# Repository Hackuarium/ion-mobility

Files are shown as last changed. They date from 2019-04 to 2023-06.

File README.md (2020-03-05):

# What is Ion Mobility Spectrometry ?

[https://en.wikipedia.org/wiki/Ion-mobility_spectrometry]

# Why should we do this ?

There are numerous application for IMS and it has the main advantage to work at atmospheric pressure (in constraste with mass spectrometry that requires most of the time 10-3 torr) that would make it compact and affordable.

We see the possibility to make continious monitoring of the bioreactor made by Hackuarium and situated in Cali, Colombia.

# Can we do a Ion Mobility Spectrometer our self ?

Main parts of the IMS :

- Desolvation zone : Insert and ionization of sample. 
Electrospray ionisation (ESI). Advantage : one can insert the liquid sample and ionize it through the same needle. 
Limitation : 5kV voltage source, 100uL/min flow rate through the needle. 

- Shutter : Let the ions pass on command.
Three grid Shutter. Advantage : easy to built and to command. 

- Drift zone : Acceleration of ions.
Made by multiple electrodes connected to different voltages with the aid of a voltage divider. 
Limitation : 10kV voltage source. 

- Detection : Faraday plate.
Transconductance amplifier converts the tiny ion current into a reasonable tension.
Limitation : The current-to-tension AOP must be with very low bias current, and low noise (hence expensive). 

- Monitoring : A/D converter. 

Link to full project already made : [https://github.com/bhclowers/OS-IMS]

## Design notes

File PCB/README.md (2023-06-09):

In order to better understand the overall electrical diagram and the paper’s resistance choice, an equivalent electrical diagram of the IMS from the first electrode to the amplifier is shown below. 
<p align="center">
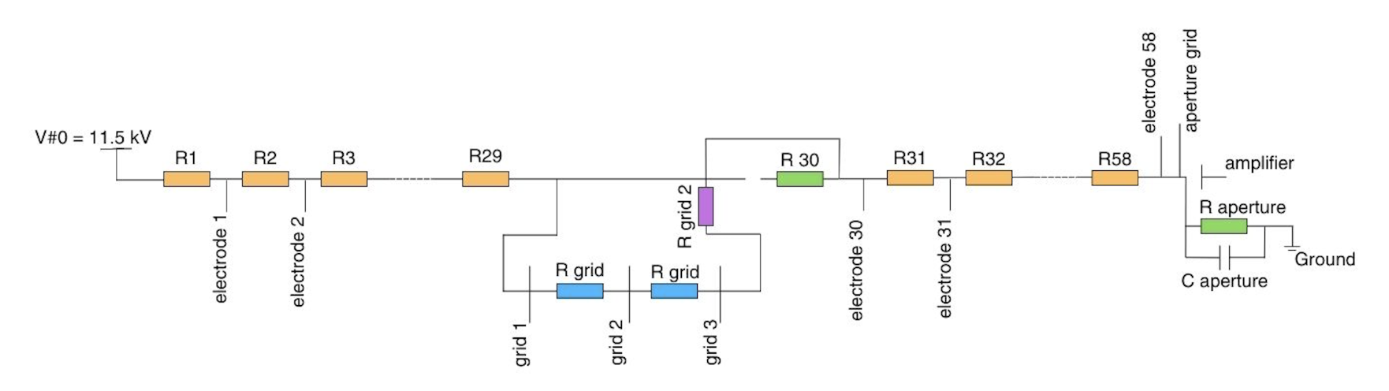
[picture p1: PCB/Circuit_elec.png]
    
</p>

Thanks to those equations, we see that when the gate is closed, the potential of the second grid is higher than when it is opened. In the paper, they recommend adding 30 to 80 V (referenced to ”small” in the equations) to stop the flow of electrons. According to the calculations, a value of 50V or higher would result in a reverse electric field and effectively close the gate. 

These calculations are based on the paper’s values, not those of the current prototype. For the moment, the resistors on the divider PCB are 10 MΩ, designed to reduce power consumption. But this does not seem necessary, since with 1 MΩ resistors, power consumption is already only 160 to 200 μA, and changing the resistor of the dividers would also mean adapting the other resistors of the circuit.

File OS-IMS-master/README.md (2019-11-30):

# APIMS
Atmospheric Pressure Ion Mobility Design

The design files located in this repository comprise the working design files used for the atmospheric pressure ion mobility spectrometer operated at Washington State University (Dr. Brian Clowers) and Azuza Pacific University (Dr. Eric Davis). Periodic updates will be pushed as modifications are made.  A wiki will be populated for the next version of the system is constructed to provide other researchers with a detailed set of assembly instructions. 

<p align="center">

</p>

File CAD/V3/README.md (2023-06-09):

# CAD design files

## Description

This folder contains all CAD design files for the V3 3D printed version of the IMS. This version is designed to hold the electrodes together in place with the divider PCBs, the target and an extension to choose the number of electrodes wanted (29 per region). It's an upgraded version of V2, capable of accommodating the 3-grid ion shutter, the aperture grid and a chamber on the backside of the target for the inlet drift/carrier gas.

It is designed to be modulary and partially modified if necessary without needing to redo and reprint the whole device.

- All the files are in 3 different versions : 
1. .SLDPRT, aka Solidworks (software used initially)
2. .STEP, to be able to open them in most CAD softwares
3. .3mf, the standard manufacturing file to 3D print with a FDM printer (e.g. prusa)

NB: The "Cible" (i.e. target) and electrode PCBs are the same one as in the V2 version, thus they are the same files as in the V2 folder. The divider PCB is different, because it is the 29 electrode slots version, as per the paper.

## Specifications

The desolvation and drift regions can hold 29 electrodes each.  
Every 2 electrodes have the same distance in between them, i.e. 0.8 mm. This ensures that the electric field is linear and continuous throughout the whole device.

The ESI needle (needs to be 3-4 kV higher in potential than the first electrode) can be mounted in front of the desolvation region.

A Nafion membrane is commonly used in IMS to separate ionized gases from other gaseous species and prevent measurement disturbances. Here are a few reasons why this membrane is used:
1. Ion selection: the Nafion membrane is selective for H+, Na+, K+ and NH4+ cation ions. It therefore selects the ions of interest for measurement, while rejecting other non-ionized or uncharged gaseous species.
2. Gas separation: the Nafion membrane is permeable to gases, but only allows high-mobility gases such as H2, N2, O2 and H2O to pass through. It therefore prevents low-mobility gases, such as noble gases, from entering the measurement zone and interfering with the results.
3. Impurity removal: the Nafion membrane can remove impurities from gases by exchanging the cations present on its surface with the impurities. It is therefore useful for eliminating contaminants that could interfere with measurement.

In our case, the membrane is mainly used for ion selection. In fact, it allows us to have only the species of interest in our spectrometer, and therefore more reliable results. The membrane is placed between the needle and the first electrode. 

Our membrane specifications:  
*Model: Nafion 117*  
*Thickness: 183 µm*  
*Density: 360 g/m2*  
*Conductivity: 0.083 S/cm*  
*Exchange capacity: 0.89 meq/g*  
*Size: 40 mm diameter circle*  

Below is a close up picture of the exploded 3-grid ion shutter :

<p align="center">
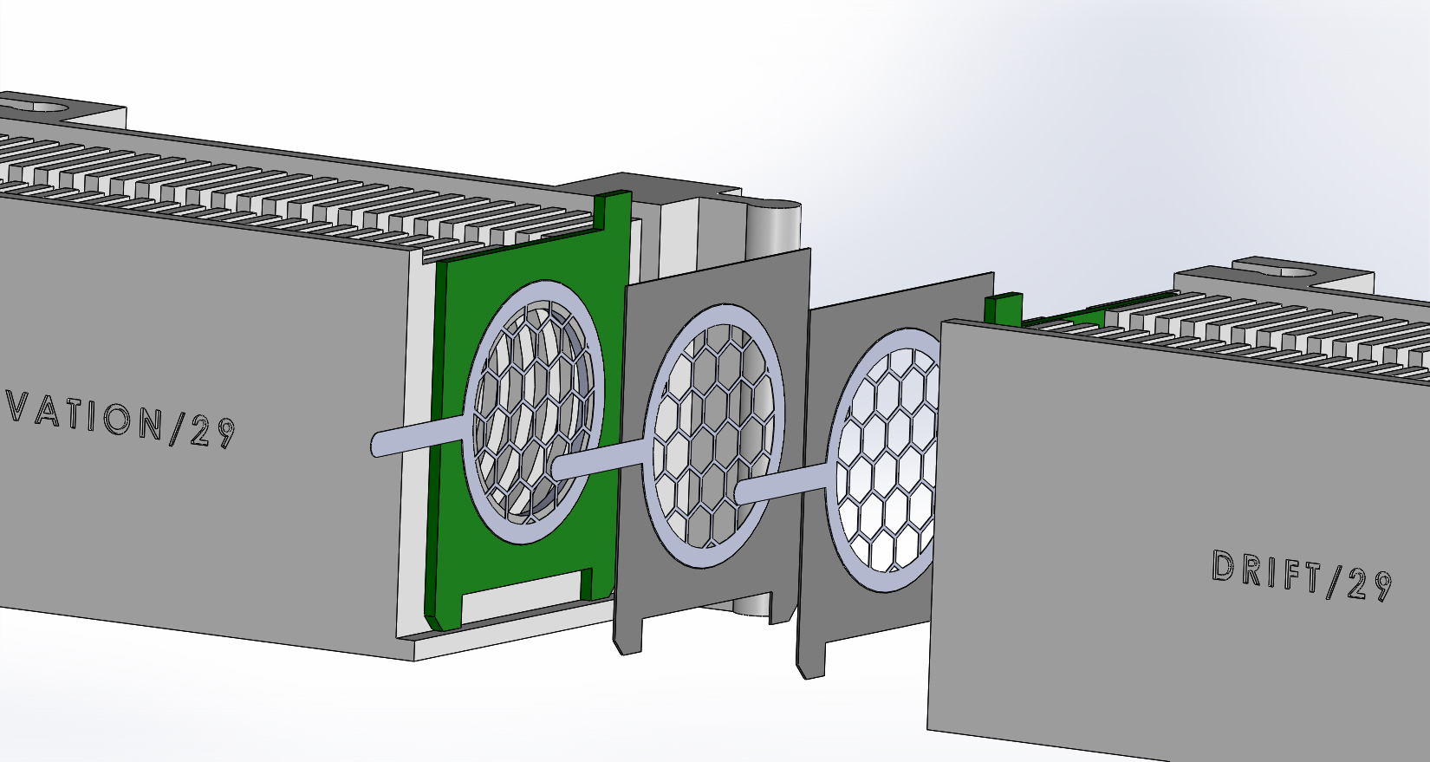
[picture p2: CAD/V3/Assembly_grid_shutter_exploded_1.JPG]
  
</p>

## Current limitations

This version hasn't been printed because we do not have the grids nor the grid spacers yet. The spacers are supposed to be 0.3mm thick, made of basically any non conductive material, and the grids are 0.1mm thick, made of stainless steel (NB: the grids in the assembly have a coarser grid with a bigger honeycomb pattern to lighten the computationnal render).

<p align="center">
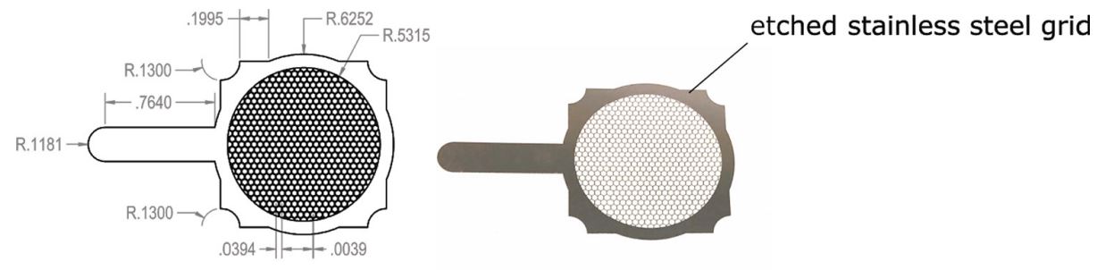
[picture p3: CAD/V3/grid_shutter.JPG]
  
</p>

## Target/Cible

The target ("Cible") is mounted at the end of the IMS, and has a hole on its back side to connect the amplification PCB as well as a hole on its top to put a tube inlet for the drift/carrier gas.

## CAD designed device

Here is shown the model of the V3 version of the CAD casing. It is a revised version with room to accommodate for the 3-grid on shutter, the aperture grid and the gas chamber for the target. The desolvation and drift regions have here 29 electrode slots each (the extension is thus not needed here and the ESI needle can be put in front directly).

<p align="center">
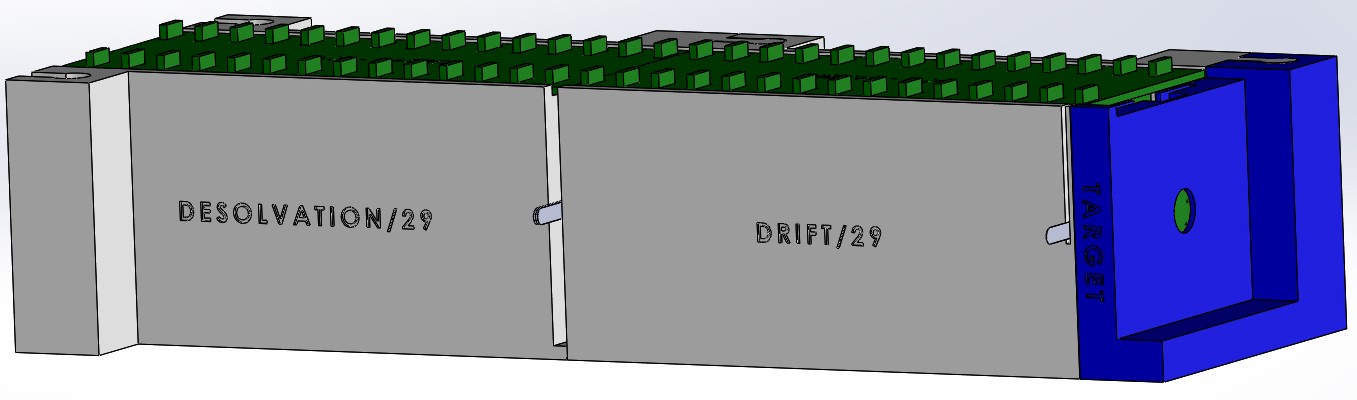
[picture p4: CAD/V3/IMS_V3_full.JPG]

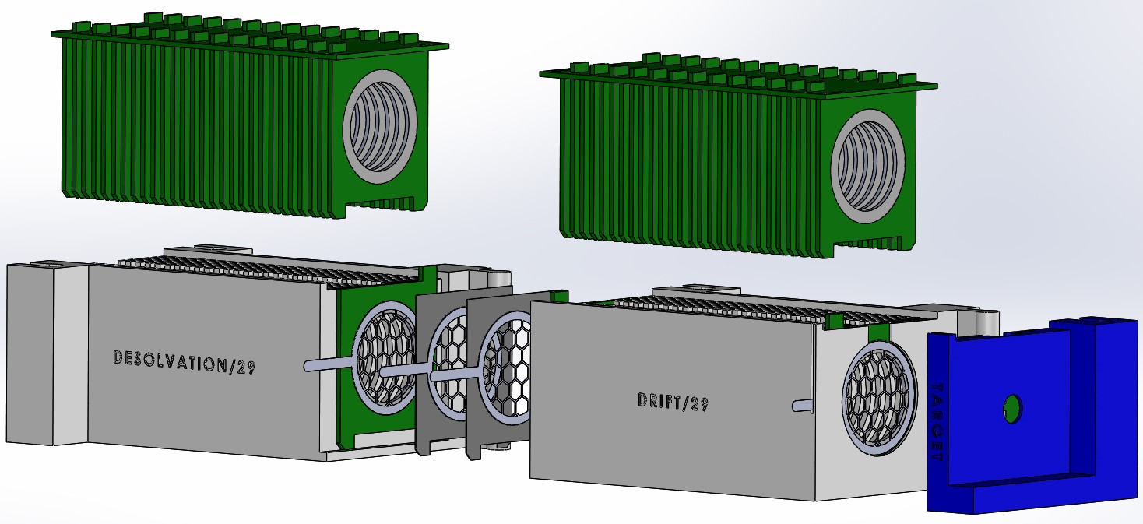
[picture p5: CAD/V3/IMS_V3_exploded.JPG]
   
</p>

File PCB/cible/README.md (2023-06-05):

# Target/Cible

## Description

Target at the end of the IMS/Drift tube, on which the ions will collide and create a small current. Is situated after the drift tube and before the amplification.

The target is a [Faraday plate](https://en.wikipedia.org/wiki/Faraday_cup) used to catch the ions and analyze them afterwards.

## Specifications and limitations

The target has to be surrounded by a ground connected ring with small holes to inject a drift gas. It is connected on its back side to the amplifier to transform the ion current into a readable voltage.

## PCB

Below are pictures of the target PCB. 

<p align="center">
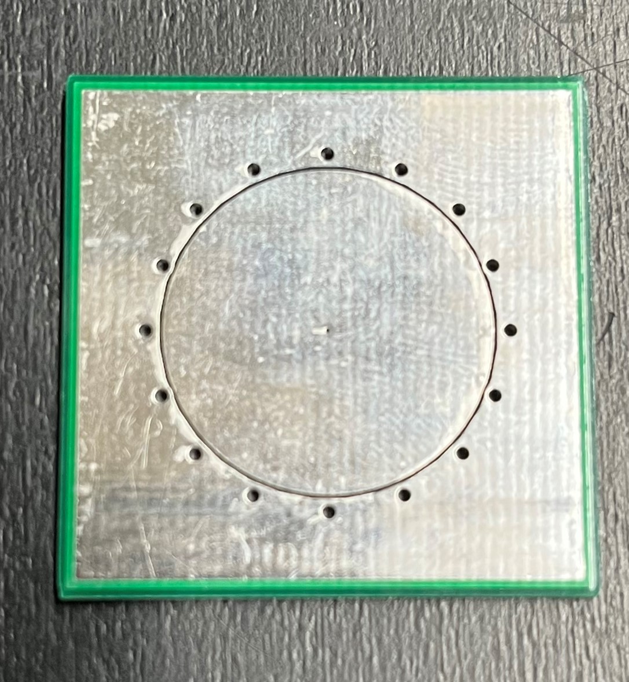
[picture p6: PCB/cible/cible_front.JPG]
    
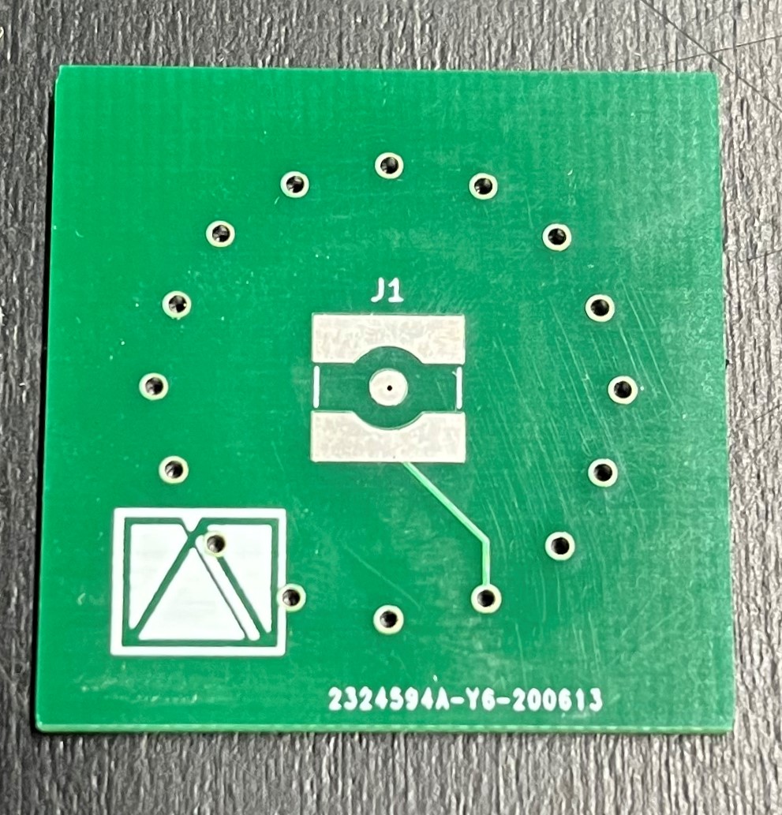
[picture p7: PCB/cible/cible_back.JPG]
    
</p>

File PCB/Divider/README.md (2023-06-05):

# Divider

## Description

Printed circuit board of the two voltage dividers for the desolvation region and the drift tube/region. Connects all electrodes together with 10 M $\Omega$ in between each of them, to create a continuous voltage gradient and thus an electric field to accelerate the ions. 

## Specifications and limitations

The highest voltage is 11.5 kV at the first electrode, down to the ground connected last electrode, and the target at the end of the drift tube.

Higher resistors in between the electrodes doesn't change the voltage gradient but reduces the current and thus the electrical consumption.

## PCB

Below are pictures of the PCBs. First one is desolvation region and second one is drift region.

<p align="center">
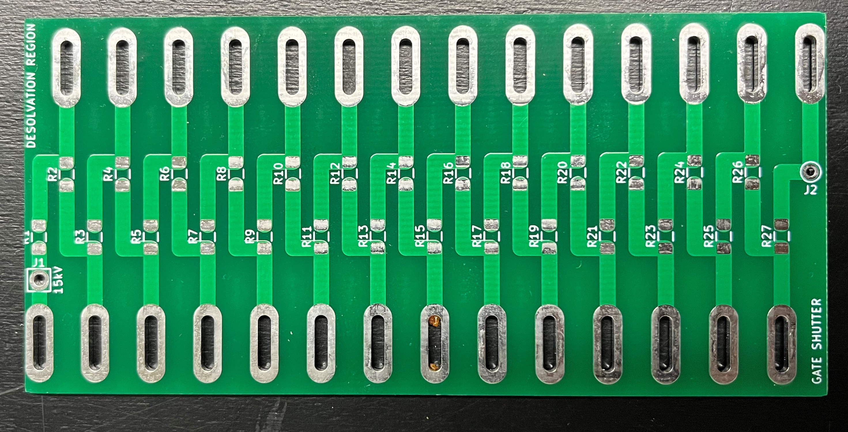
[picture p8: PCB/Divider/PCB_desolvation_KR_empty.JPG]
    
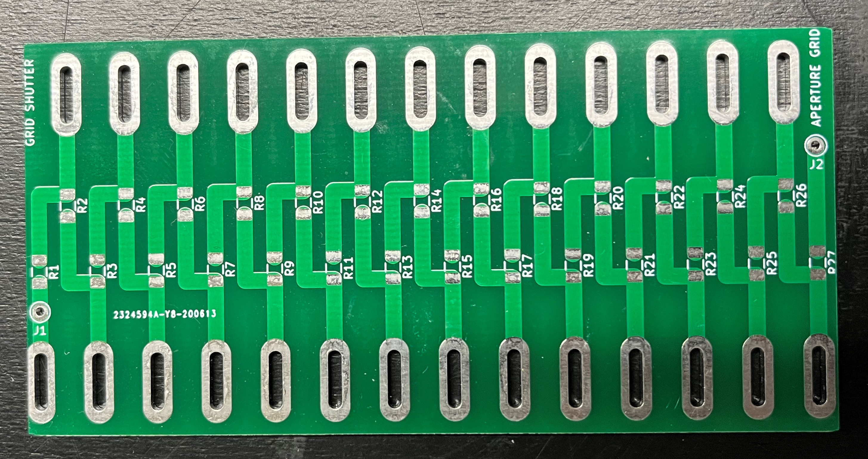
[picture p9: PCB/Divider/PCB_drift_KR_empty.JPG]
    
</p>

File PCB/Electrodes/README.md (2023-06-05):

# Electrode PCB

## Description

Here are all the PCB files related to the electrodes.

## PCB

Below is a picture of the PCB. 

<p align="center">
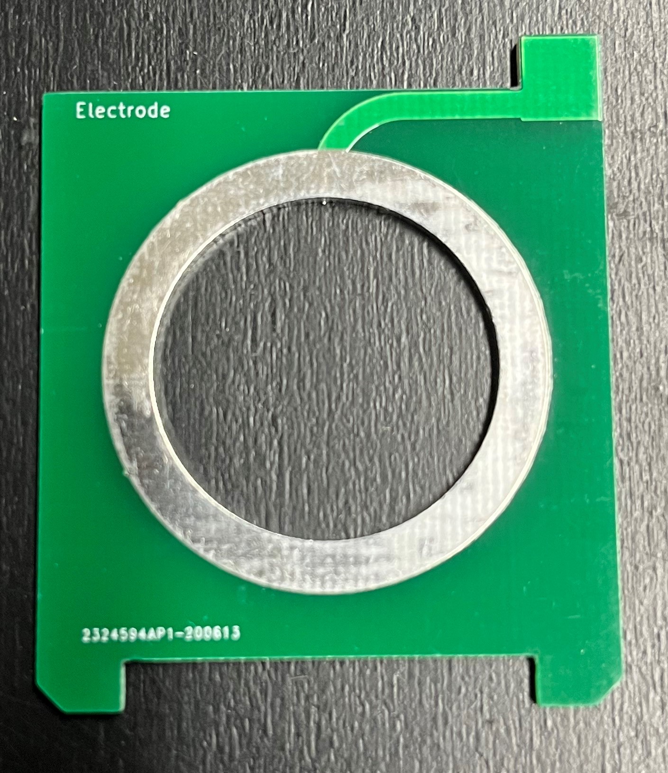
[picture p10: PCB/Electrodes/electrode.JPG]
    
</p>

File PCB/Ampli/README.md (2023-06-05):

# Amplification stage

## Description

Amplification stage to transform the small current on the target to an acceptable voltage to be read/processed. 

[Transimpedance circuit](https://en.wikipedia.org/wiki/Transimpedance_amplifier) with a big gain (10^8) and a voltage follower through a dual precision operationnal amplifier (Texas Instruments LMC6082).

## Specifications and limitations

The circuit needs to be as close as possible to the target of the IMS in order to limit the noise present on the signal. One possibility is to solder the PCB directly on the back of the target. 

Possible amplification of the noise must be taken into account, and possibly filtered through a very small capacitor (~0.01 pF, thus quite expensive) in the gain stage feedback loop (a bigger resistor amplifies the signal but also the noise).

## PCB

Below is a picture of the mounted PCB, currently missing the connectors and a potential filtering capacitor C1. 

<p align="center">
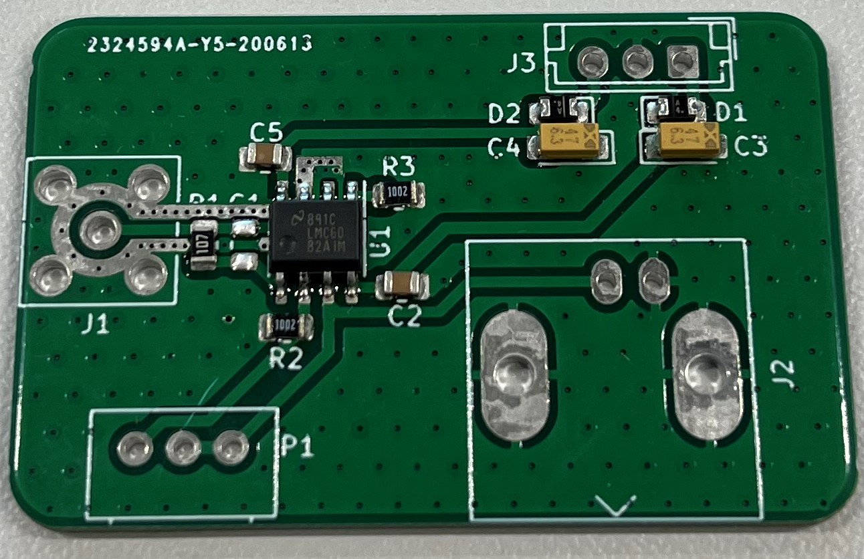
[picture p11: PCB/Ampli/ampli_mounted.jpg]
    
</p>

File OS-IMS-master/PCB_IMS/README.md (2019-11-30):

## This directory contains the latest version of the PCB IMS to be detailed in the manuscript submitted to HardwareX.  These files outline the design and assembly of a high performance, open-source Ion Mobility System

<p align="center">
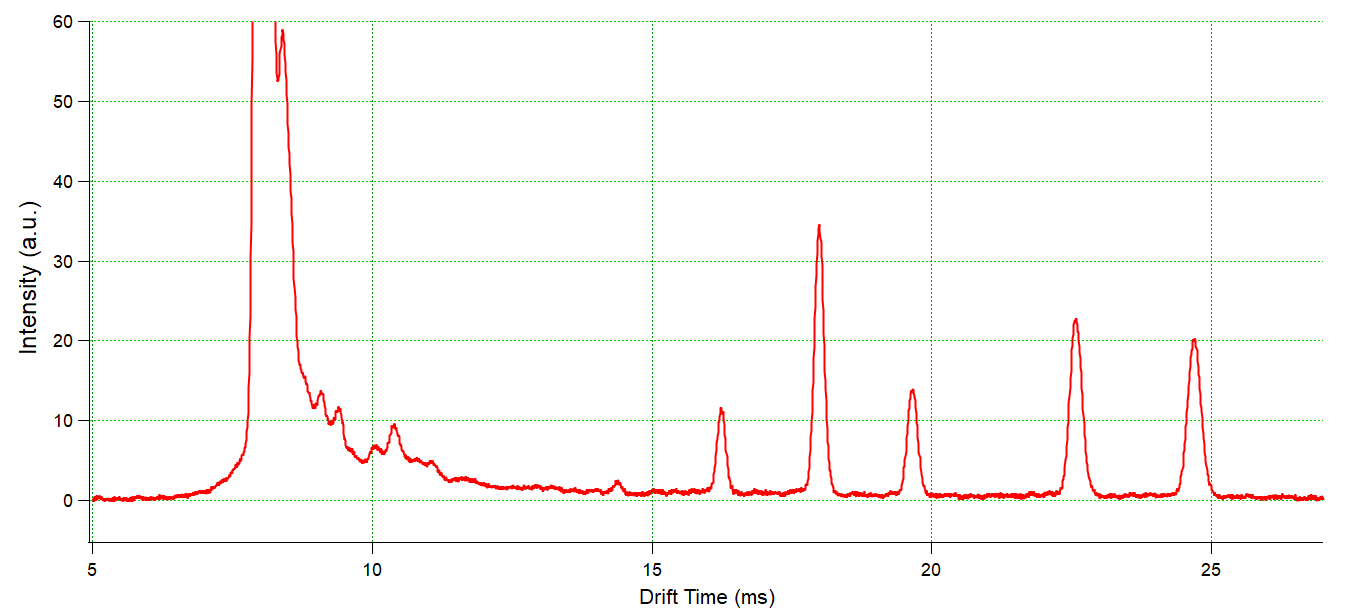
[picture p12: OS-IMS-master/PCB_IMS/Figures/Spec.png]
  </p>
</center>
<p align="center">
  </p>
</center>

#### When operated as a stand-alone device, an ion mobility spectrometer (IMS) routinely offers low limits of detection (pptv-range) for gas-phase analytes even for measurement times less than a second. Mass analyzers further enhance the analytical power of IMS separations, however, high performance drift-cell IMS instruments are often highly customized, relatively large, and require extensive expertise to operate. In this work we present an optimized, low cost IMS system that leverages an easy-to-assemble ion gating structure that enables IMS spectra with resolving powers exceeding 90 for a drift cell only 10 cm in length. The IMS presented in this work consists of stacked rings divided by spacers all fabricated from printed circuit boards (PCB). The rings are connected via a slotted PCB-board containing a surface mounted voltage divider that connects directly to the ring electrodes allowing a fast and easy assembly. This highly modular design enables e.g. the realization of variable drift tube lengths or single and dual gate setups. Instead of the commonly used Bradbury Nielsen gates, the IMS is equipped with a 3-grid ion gate allowing the generation of short (<50 μs) ion packets increasing the resolving power of the instrument. 

### License

Open Source Hardware 

The PCB-IMS is an open source project by [*Tobias Reinecke*](mailto:treinecke@gmail.com) and [*Brian Clowers*](mailto:bhclowers@gmail.com).

The use, modification, and implementation of this project is goverened by the [CERN Open Hardware Licence v1.2](LICENSE).

#### Acknowledgements:
* This work was supported in part by the National Science Foundation (CHE-1506672) and DTRA (Award Number: HDTRA1-14-1-0023)
* We would also like to acknowledge the dedicated, prolific, and timeless efforts of [*Gordon A. Anderson*](https://github.com/GordonAnderson).

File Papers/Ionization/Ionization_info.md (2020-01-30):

# Non - Radioactive ionization 

- Désorption-ionisation laser assistée par matrice : [https://fr.wikipedia.org/wiki/D%C3%A9sorption-ionisation_laser_assist%C3%A9e_par_matrice] (No gate needed?!)
- UV LED Ionization : [UV_LED.pdf] Attention, check the results they got....
- Compact electrospray : [electrospray.pdf]
- IMPORTANT : [1.1645286.pdf]

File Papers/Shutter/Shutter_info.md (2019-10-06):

# Shutter info 

Le Shutter va énormément influer la qualité de la spectrométrie : 
Shutter time augmente => résolution diminue 

2 Types de Shutter : 
-  Bradbury-Nielsen [https://en.wikipedia.org/wiki/Bradbury%E2%80%93Nielsen_shutter]
-  Tyndall−Powell [chen2017.pdf]
- Field-switching shutter [Bradbury-NielsenVSField-switching.pdf] (attention : difficult with ion sources like Nickel-63 or UV sources and these shutters require a field free ionization region when the shutter is closed => no corona no electron spray, a lot of the design complexity has been moved to the electronic switching circuit)
- Tristate shutter [kirk2018] (low microsecond range)

BN : TB mais compliqué à faire (2 grilles entremêlées avec un potentiel différent à chaque grille dévie les ions)
TP : + Facile à faire (2 grilles espacées qui n'ont pas besoin d'être bien alignées). 
-> Bcp moins précis car l'espace entre les grilles forme une zone de déplétion (sans charge) que les ions les plus lourds n'ont pas le temps de traverser si le shutter time est petit (càd à grande résolution). Les ions les + lourds sont dont anihilés à la fermeture du gate, avant d'avoir pu traverser la zone. 

=> VOIR chen2017.pdf POUR SOLUTION POSSIBLE : Augmenter la diff de potentiel afin d'accélérer + les ions entre les deux grilles et donc les + lourds arrivent à passer. 

Note : GPV stands for the gate penetration voltage defined as the voltage difference between the two grids of the TPG at open status, while GCV stands for the gate closing voltage defined as the extra voltage superposed on the original potential of Grid 2 for closing the TPG.

-> Increase GPV to smaller the depletion zone width.

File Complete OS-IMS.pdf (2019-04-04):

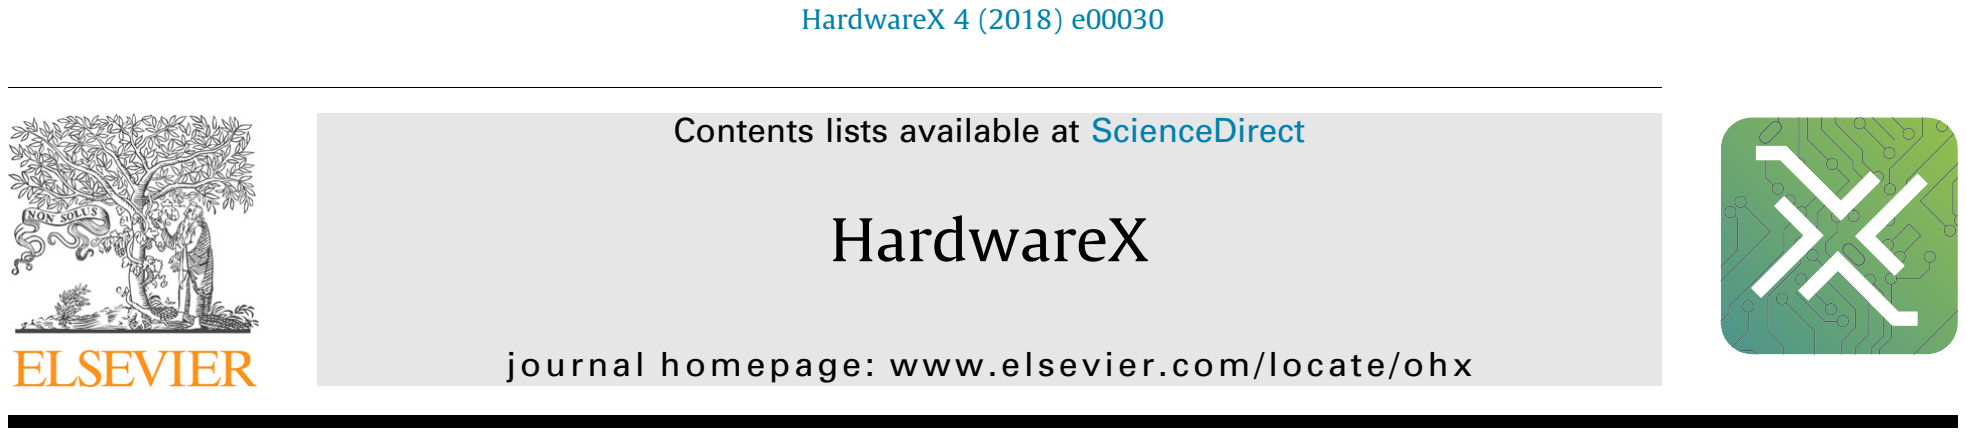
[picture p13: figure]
HardwareX 4 (2018) e00030; Contents lists available at ScienceDirect; HardwareX; journal homepage: www.elsevier.com/locate/ohx

### Hardware Article

## Implementation of a flexible, open-source platform for ion mobility spectrometry

## Tobias Reinecke, Brian H. Clowers ⇑

Department of Chemistry, Washington State University, Pullman, WA 99164, United States

## article info

Article history:
Received 2 April 2018
Received in revised form 8 May 2018 Accepted 9 May 2018

Keywords:
Ion mobility spectrometry
Chemical instrumentation
Laboratory instrumentation Trace analysis

## abstract

When operated as a stand-alone device, an ion mobility spectrometer (IMS) routinely offers low limits of detection (pptv-range) for gas-phase analytes even for measurement times less than a second. Mass analyzers further enhance the analytical power of IMS separations, however, high performance drift-cell IMS instruments are often highly customized, relatively large, and require extensive expertise to operate. In this work we present an optimized, low cost IMS system that leverages an easy-to-assemble ion gating structure that enables IMS spectra with resolving powers exceeding 90 for a drift cell only 10 cm in length. The IMS presented in this work consists of stacked rings divided by spacers all fabricated from printed circuit boards (PCB). The rings are connected via a slotted PCB-board containing a surface mounted voltage divider that connects directly to the ring electrodes allowing a fast and easy assembly. This highly modular design enables e.g. the realization of variable drift tube lengths or single and dual gate setups. Instead of the commonly used Bradbury Nielsen gates, the IMS is equipped with a 3-grid ion gate allowing the generation of short (<50 ls) ion packets increasing the resolving power of the instrument.
2018 Published by Elsevier Ltd. This is an open access article under the CC BY-NC-ND license (http://creativecommons.org/licenses/by-nc-nd/4.0/).

Specifications table

Hardware name | Ion Mobility Spectrometer
Subject area | Chemistry and Biochemistry
| Environmental, Planetary and Agricultural Sciences
| Educational Tools and Open Source Alternatives to Existing Infrastructure
| General
Hardware type | Measuring physical properties and in-lab sensors
| Biological sample handling and preparation
| Field measurements and sensors
| Electrical engineering and computer science
| Mechanical engineering and materials science
Open Source License | CERN OHL v.1.2 (https://www.ohwr.org/licenses/cern-ohl/license_versions/v1.2)
Cost of Hardware | $210 USD for the PCB-IMS and high speed, high gain amplifier
Source File Repository | OSF Link: https://osf.io/p6d4x/Github: https://github.com/bhclowers/OS-IMS

https://doi.org/10.1016/j.ohx.2018.e00030
2468-0672/ 2018 Published by Elsevier Ltd.
This is an open access article under the CC BY-NC-ND license (http://creativecommons.org/licenses/by-nc-nd/4.0/).

⇑ Corresponding author.

E-mail address: brian.clowers@wsu.edu (B.H. Clowers).

Warning: Exercise extreme caution when operating and working around the PCB IMS system. Be vigilant regarding the voltage potentials used and the current necessary to drive the unit. Establish appropriate engineering controls to shield the system.
To operate the described PCB IMS it needs to be connected to a high voltage power supply. During operation, conductors at dangerous voltages may be exposed. Extreme care should be taken to protect against shock. Stand on an insulating pad and use only one hand when checking components. Always work with another person in case an emergency occurs. Any work on an operational system should only be executed after the high voltage connectors have been disconnected and the power deenergized.
1. Hardware in context

Ion mobility spectrometry is a gas-phase separation technique that finds utility across analytical domains [1–4]. Most notably, this technique supports many of the field-based detection platforms used to screen passengers, baggage, and goods for explosives and narcotics [5]. Select IMS instruments also find extensive use as point detectors for chemical warfare agents [6]. The wide use of IMS in the field is largely predicated on its relative speed, chemical selectivity, and capacity to operate without expensive vacuum pumps. The sensing principle of IMS is based on a separation of ions by their ion-specific velocity in a drift gas under the influence of an electric field. Compared to other laboratory approaches that probe gas-phase ions, such as mass spectrometry [7], ion mobility systems currently have yet to realize the same levels of resolution. Nevertheless, they serve a critical role as a screening tool. It is important to recognize that the primary role of devices such as IMS is to minimize false negatives where such outcomes are untenable. From a fundamental science perspective, IMS devices also serve as key tools for probing ion-neutral interactions, gas-phase chemistry, and thermodynamic properties of clusters not accessible using other approaches [7–10].
Despite their wide deployment and importance to fundamental science, there are few literature reports detailing the construction and operation of a high-performance, drift-tube ion mobility system. For reference, there are a range of analytical techniques that exploit the property of gas-phase ion mobility to separation ions but the drift tube system arguably provides the largest degree of flexibility, resolution, and accuracy. Conceptually, drift-tube IMS hardware is simple but construction of such devices that produce consistent results has proven challenging and often relied upon a select set of skills, access to resources, and tribal knowledge. In its simplest form, drift tube IMS systems are comprised of an ionization source, reaction/desolvation region, ion gate, drift cell, and detector. Supporting components also include a stable high voltage power supply, ion gating electronics, and a high speed, high-gain current to voltage converter. In the present embodiment of the drift tube IMS, we detail an easily manufactured, open-source drift tube design that incorporates a robust 3-grid shutter design that greatly eases assembly and still enhances performance compared to the traditionally used Bradbury Nielsson Ion gate [11]. In order to maximize the analytical performance, the design process for the size of electrodes, spacers and detector followed the general guidelines given by Bohnhorst et al. [12]. As demonstrated in the latter sections of this report, the IMS system used in this report is capable of attaining resolving powers above 90 for a 10 cm drift cell which exceeds the performance of most commercial systems with a similar footprint. Additional IMS elements included in this design are the drift gas inlet (used to control the local gas-phase environment), detector assembly, and a high-speed, high-gain current to voltage converter. Though a control system is left to the user (a traditional oscilloscope will often suffice), we make recommendations and provide guidance on such tools. It should also be noted that another key element of the drift-tube IMS system not covered in this communication is the ion gate pulser. However, in a separate report [13], we detail the operation and performance of an open-source unit capable of supplying that information.
2. Modular drift tube description and assembly

In this section the assembly of the PCB desolvation and drift region as shown in Fig. 1 is described. In a first step, the electrode alignment board (Fig. 2) is equipped with resistors, specifically surface mount 1206 components. For the presented IMS, 1 MO ± 1% resistors were used, but more important than the value of the resistor is to consider sufficient voltage ratings. A 10.4 cm drift tube (or desolvation region respectively) consists of 29 electrodes (Fig. 3) and 56 spacers (Fig. 4).
The distance between two electrodes and the inner diameter of the ring electrodes and spacers were chosen according to Bohnhorst et al. in order to realize a homogeneous electric field inside the drift tube enabling to utilize ions within 90% of the inner electrode radius [12]. These design consideration allow the size of the detector to be maximized without broadening of the ion peaks due to field inhomogeneities in close proximity to the electrodes. Therefore, this design leads to an optimum balance between sensitivity and resolving power.
The electrodes and spacers are stacked on rods (we used poly ether ether ketone (PEEK) rods with a 6 mm diameter and threaded ends though any appropriate, non-conducting material would suffice), beginning with an electrode followed by two spacers as shown in Fig. 5. This alternating pattern of 2 spacers to 1 electrode is repeated to achieve the desired drift cell length. Finally, the electrode alignment board is set on top of the stack and the electrode contacts are soldered to the connectors on the alignment board. To achieve higher stability of the setup it is advantageous to connect a second electrode alignment board without resistors to the bottom of the stack. To prevent misalignment of the electrodes and spacers, soldering of the electrode alignment board should only be conducted when the spacers and electrodes are aligned on the
2 | T. Reinecke, B.H. Clowers / HardwareX 4 (2018) e00030

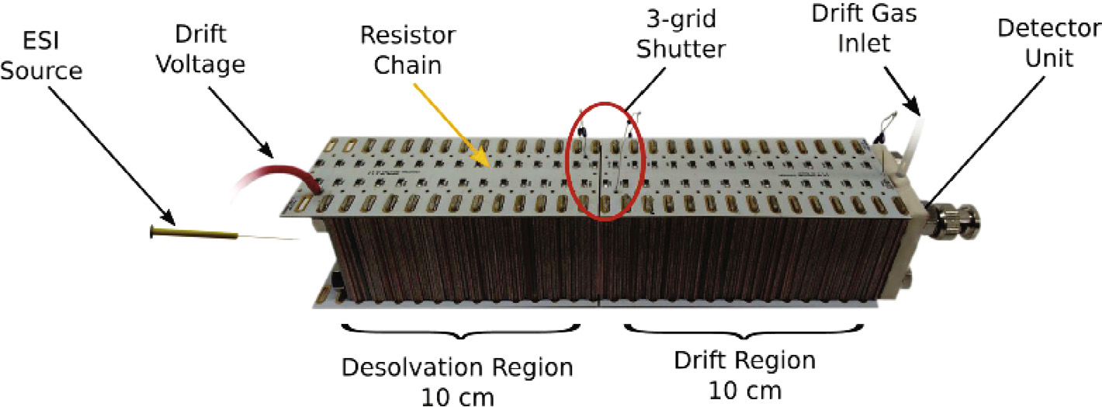
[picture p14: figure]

Fig. 1. Photo of the PCB-IMS assembly. Labeled are the pertinent components needed for operation. Details for all of the components, aside from the ion source (as that can vary depending on upon the application) are detailed in this communication.

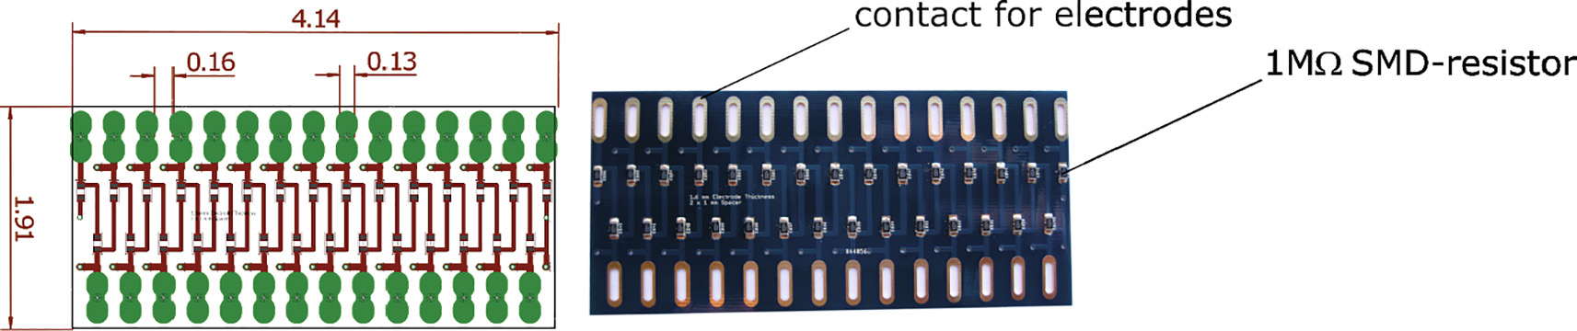
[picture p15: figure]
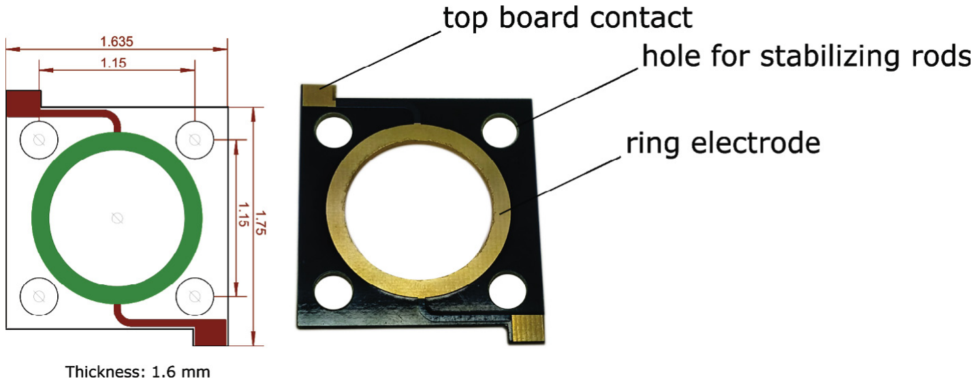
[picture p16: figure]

Fig. 3. Schematic and photo of an electrode used to realize a homogeneous electric field inside the drift tube.

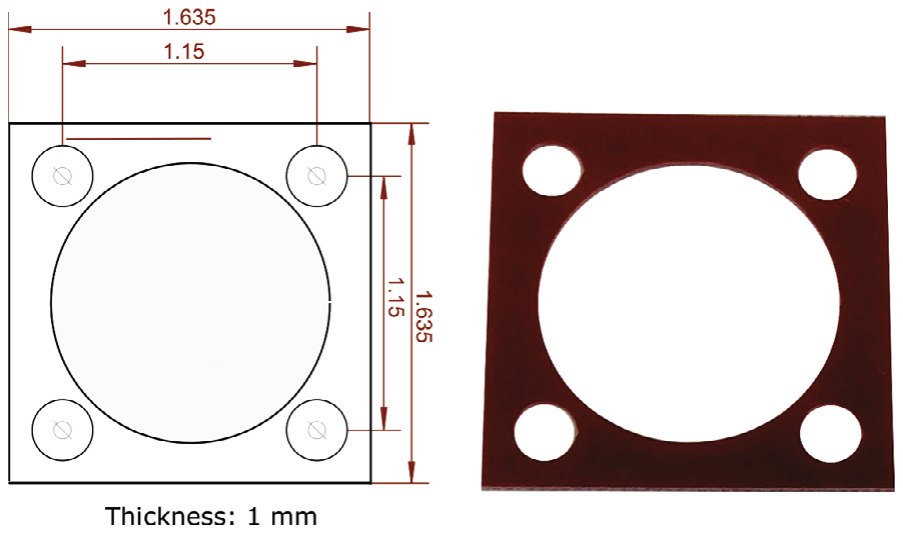
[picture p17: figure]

Fig. 4. Schematic and photo of a spacer used to distance two electrodes.

Fig. 2. Schematic and photo of the electrode alignment board. The layout of this board connects each subsequent electrode into a resistor chain established by the surface mount resistors.

T. Reinecke, B.H. Clowers / HardwareX 4 (2018) e00030 | 3

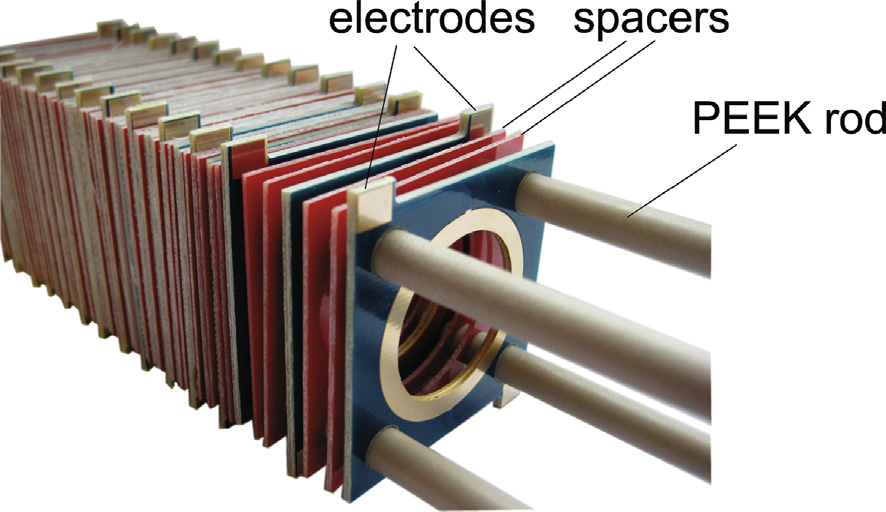
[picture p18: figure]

previously described alignment rods. It should be noted, that the PCB manufacturing process and soldering may create a dirty system. Therefore it is important to clean the drift tube to enable the measurement of clean spectra. Isopropanol was used to clean the parts and subsequently placed the assembled drift tube in a vacuum oven at elevated temperature (180 F). It is also worth mentioning that the spacing of the electrodes was chosen to optimize the homogeneity of the resulting electric field when connected to a resistive divider. However, upon assembly the system is not necessarily air tight. To seal the system a higher degree of compression would be needed along with a different top board (Fig. 2.). Nevertheless, with a positive pressure of gas moving through the system the gas within the cell may be kept relatively clean. If a particular experiment requires a sealed system it is surely possible to place the system within a second enclosure.

2.1. 3-Grid ion shutter

To inject short ion packages from the desolvation region into the drift region, an ion shutter is necessary. A commonly used ion shutter is the Bradbury Nielsen ion gate [15]. It consists of a parallel set of wires, which are set to opposite potentials in order to create a field orthogonal to the drift field and thus stopping the ions from entering the drift region. However, as the manufacturing of this type of gate is time and resource intensive, not to mention extreme levels of patience, we employ a different type of ion shutter which was first introduced by Langejuregen et al. and shown to provide favorable levels of performance for electrospray ion mobility spectrometry [14,16]. Fig. 6 depicts a schematic of the employed

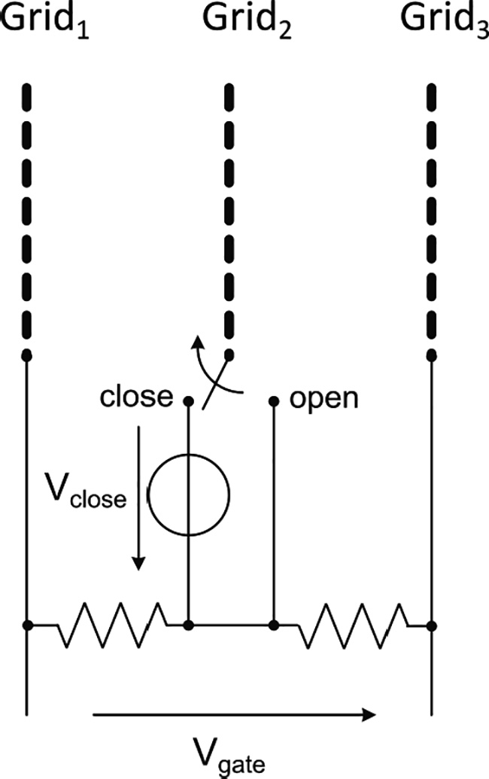
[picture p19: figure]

Fig. 6. Schematic of the 3-grid ion shutter. Compared to the traditional ion gate, the static grid structure eases assembly and operation [14]. In the open state the potential of the center grid (Grid2) is held at a value equal to the center potential between Grid1 and Grid3. The gating electronics are detailed in a separate manuscript and allow for the modulation of this floated potential [13].

Fig. 5. Stack of electrodes and spacers on centering PEEK rods.

3-grid ion shutter. It consists of 3 grids separated by spacers. Grid1 and Grid3 are connected via two equal resistors. To realize a field in the open shutter equal to the field in drift and desolvation region, the used resistors should have a value of 150 kO, when using 1 MO on the electrode alignment board. When the gate is open, Grid2 is connected to the center potential between Grid1 and Grid3, creating a field gradient that is allowing ions to pass from desolvation region to drift region. To close the gate, Grid2 is connected to a higher potential and therefore the electric field between Grid1 and Grid2 is reversed and stopping the ions from entering the drift region while the field in drift and desolvation region stays constant as the potential on Grid1 and Grid3 remains unchanged. The voltage necessary to stop the ions depends on the field strength in the ion gate and typically ranges between 30 V and 80 V. It can be advantageous to stabilize the voltage on Grid1 and Grid3 with a capacitor (capacitor gate 4700 pF 10 kV) connected to the respective gate and ground.
Fig. 7 shows the stainless steel grid we used to implement the 3-grid ion shutter. The thickness of the grid is 0.1 mm and was produced in a photo chemical etching process by Newcut (Newark, NY). Fig. 8 shows a photo of the 3-grid shutter. Grid1 is in direct contact with the last electrode of the desolvation region. Then a 300 mm PTFE spacer is inserted, followed by Grid2, another PTFE spacer and Grid3. For reference the PTFE spacer can be constructed using a pair of scissors and a ¼” hole punch, or for those more enterprising, an electronic scrapbook cutter. The footprint of each PTFE spacer conforms to the standard 1 mm PCB spacer detailed in Fig. 4.
2.2. Integrated Faraday detector and drift gas inlet

The detector consists of a Faraday plate enclosed by a ground plane, see Fig. 9. To enable an evenly distributed flow of drift gas over the cross section of the drift tube, the Faraday plate is surrounded by pinholes which serve as drift gas inlets. On the backside, the Faraday plate is connected to the inner conductor of an SMA connector and the ground plane to the outer conductor respectively. To realize a connection from the detector to the drift gas supply, 3 spacers with a small cut-out are stacked on the backside of the detector, as shown in Fig. 10. Subsequently, a 1/1600 ID Teflon hose is placed in the cutout. As depicted in Fig. 11, the backplate is then placed on the stack of spacers and sealed with an O-ring. Finally, the Teflon hose is glued in for better seal and stability. Note that it is important to use an adhesive with low vapor pressure in order to keep the drift gas free from contamination. A suitable choice is TorrSeal.
To shield the detector from an image current induced from the approaching ion cloud, the drift tube is terminated with an aperture grid which is directly placed on the last electrode, followed by 1 spacer and finally the detector. The aperture grid is

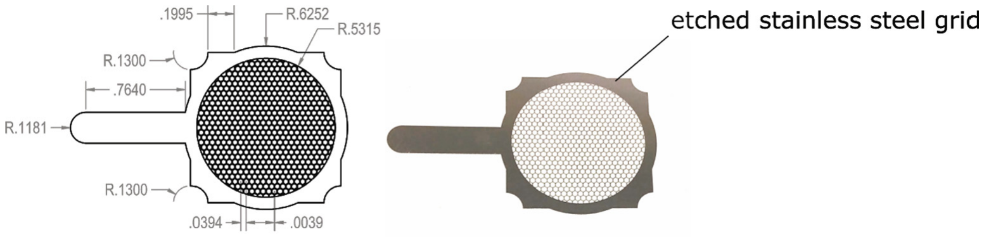
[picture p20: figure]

Fig. 7. Schematic and photo of the etched stainless steel grid.

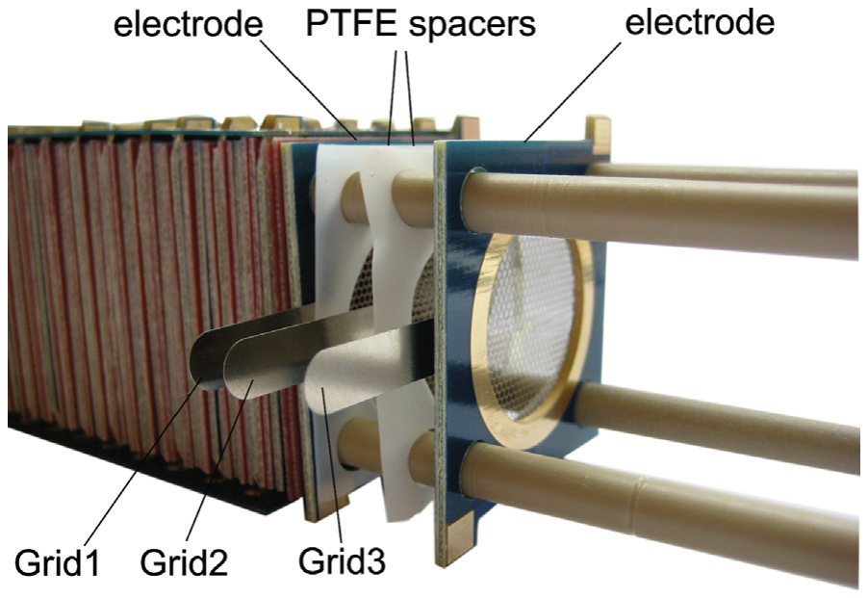
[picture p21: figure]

Fig. 8. Photo of the 3-grid ion shutter.

T. Reinecke, B.H. Clowers / HardwareX 4 (2018) e00030 | 5

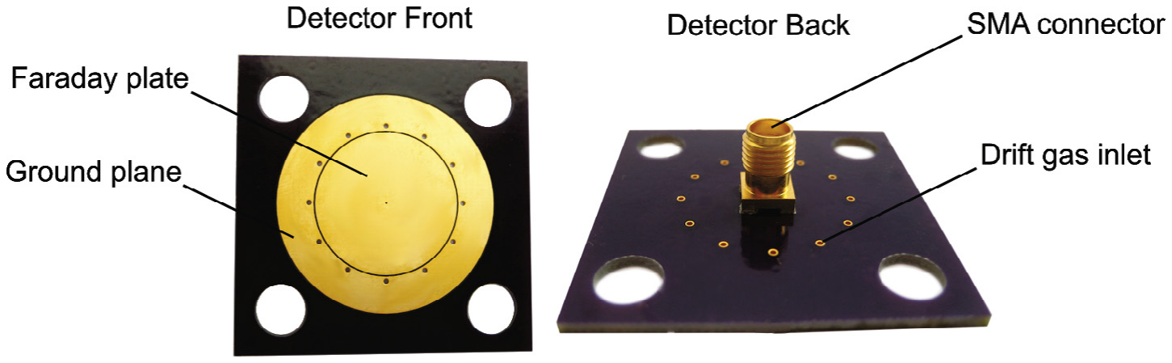
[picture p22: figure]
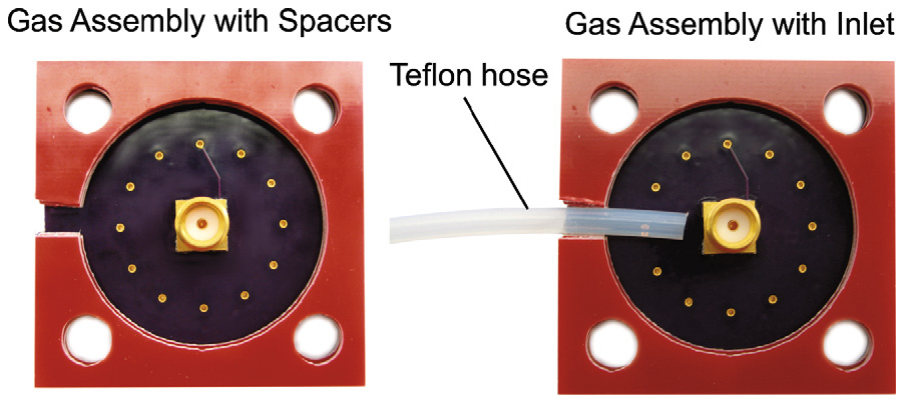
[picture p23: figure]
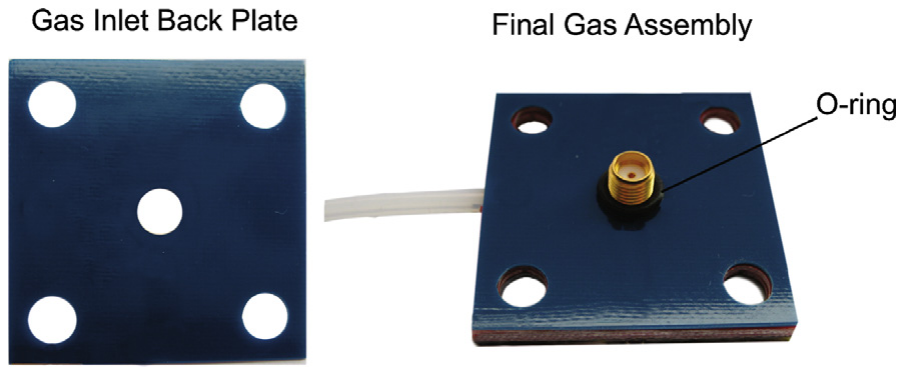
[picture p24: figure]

connected via a 500 kO resistor to ground, as shown in Fig. 12. To stabilize the voltage on the aperture grid, it is advantageous to add an additional capacitor (we used 0.22 mF) in parallel to the resistor.

2.3. Amplifier

To amplify the current produced by the ions discharging on the Faraday plate, a transimpedance (current to voltage) amplifier is necessary. The amplifier described in this section is shown in Fig. 13. It has a variable gain that can be set to either 10⁸ or 10⁹
The Schematic is depicted in Fig. 14. To achieve the maximum gain, this amplifier uses two stages. Stage 1 consisting of an operational amplifier and the resistor R1 provides a current-to-voltage amplification of R1 = 10⁸ O. The resistor R2 was added to protect the input of the operational amplifier. However, it might not be necessary to use R2. When the switch is set to ‘‘1e8” (as depicted in the schematic), the output signal of Stage 1 is fed to Stage 2a which only consists of 1 operational amplifier (A) and resistor R6. The output of this operational amplifier is directly fed back to the negative input leading to an amplification of 1 and thus to an overall amplification of 10⁸
. However, Stage 2a acts as a voltage follower (buffer amplifier) to achieve an amplifier performance that is independent of the current drawn from the load (in this case the data acquisition system). When the switch is set to ‘‘1e9”, the output signal of Stage 1 is fed to Stage 2b. Under this scenario, the output voltage of the operational amplifier (B) is divided by the voltage divider consisting of R3, R4 and R5 to (R3||R5)/((R3||R5) + R3) = 1/10 and fed back to the negative input of (B). Thus, an additional amplification of 10 is realized leading to an overall amplification of 10⁹
. The rise time of the amplifier critically depends on the input capacitance, but in normal operation a rise time of approximately 20 ms is easily achievable which is sufficient to amplify the ion current without adding significant broadening to the ion peak.

Fig. 9. Faraday plate with SMA-connector.

Fig. 10. Spacers are stacked on the backside of the detector and a Teflon hose is put in place.

Fig. 11. The detector is sealed with a backplate and O-ring.

3. Design files summary

Primary Source Location: https://github.com/bhclowers/OS-IMS/tree/master/PCB_IMS

Design file name | File type | Open source license | Location of the file
1a_Spacers.brd | Eagle file | CERN OHL v1.2 | https://github.com/bhclowers
1b_Spacer.STL | STL file | CERN OHL v1.2 | https://github.com/bhclowers
2a_Electrodes.brd | Eagle file | CERN OHL v1.2 | https://github.com/bhclowers
2b_Electrode.STL | STL file | CERN OHL v1.2 | https://github.com/bhclowers
3_electrode alignment board.brd | Eagle file | CERN OHL v1.2 | https://github.com/bhclowers
4_Detector.brd | Eagle file | CERN OHL v1.2 | https://github.com/bhclowers
5_detector backplate.brd | Eagle file | CERN OHL v1.2 | https://github.com/bhclowers
6_Grid.STL | STL file | CERN OHL v1.2 | https://github.com/bhclowers
7_schematic amplifier.dch | diptrace file | CERN OHL v1.2 | https://github.com/bhclowers
8_layout amplifier.dip | diptrace file | CERN OHL v1.2 | https://github.com/bhclowers
9_amplifier_gerbers.zip | Zipped Gerber Files | CERN OHL v1.2 | https://github.com/bhclowers
4. Bill of materials
Designator Component | Quantity Cost per unit USD Total
cost

Source of
materials
| Amplifier | | | $62.60
Fig. 13 | DIODE SCHOTTKY | 2 | $0.41 | $0.82 | Digikey
Fig. 13 | Capacitor 0.1UF 50 V X7R RADIAL | 4 | $0.18 | $0.72 | Digikey
Fig. 13 | Capacitor 100PF 3KV NP0 RADIAL | 1 | $2.77 | $2.77 | Digikey
Fig. 13 | Capacitor TANT 47UF 6.3 V 10% RADIAL | 2 | $1.03 | $2.06 | Digikey
Fig. 13 | IC OPAMP JFET 1MHZ 8SO | 1 | $5.13 | $5.13 | Digikey
Fig. 13 | IC OPAMP GP 1MHZ 8SOIC | 1 | $8.00 | $8.00 | Digikey
Fig. 13 | SWITCH SLIDE DPDT 50MA 48 V | 1 | $2.90 | $2.90 | Digikey
Fig. 13 | BNC JACK R/A 50 OHM PCB | 2 | $3.48 | $6.96 | Digikey
Fig. 13 | Resistor 100 M OHM 1/4W 1% AXIAL | 1 | $4.63 | $4.63 | Digikey
Fig. 13 | Resistor 10 K OHM 1/4W 1% AXIAL | 3 | $0.10 | $0.30 | Digikey
Fig. 13 | Resistor 1.13 K OHM 1/4W 1% AXIAL | 1 | $0.56 | $0.56 | Digikey
Fig. 13 | Resistor 9.09 K OHM 0.6 W 1% AXIAL | 1 | $0.29 | $0.29 | Digikey
Fig. 13 | Resistor 6.65 K OHM 1/2W 1% AXIAL | 1 | $0.61 | $0.61 | Digikey
Fig. 13 | AC/DC CONVERTER ±15 V 6 W | 1 | $22.05 | $22.05 | Digikey
Fig. 13 | PCB Board | | | $4.80 | OSHPark
| 2 10 cm Drift Tube including detector | | | $148.48
Fig. 4 | Spacers | 116 | $0.30 | $34.80 | DirtyPCBs
Fig. 3 | Electrodes | 58 | $0.35 | $20.30 | DirtyPCBs
Fig. 7 | Grids | 4 | $10.00 | $40.00 | Newcut
Fig. 2 | electrode alignment board | 2 | $3.40 | $6.80 | DirtyPCBs
Fig. 9 | detector board | 1 | $4.45 | $4.45 | OSHPark
Fig. 11 | detector back plate | 1 | $0.30 | $0.30 | OSHPark
Fig. 5 | rods | 4 | $2.00 | $8.00 | McMaster
capacitor aperture grid (.22uF 2000 V 10%) 1 | $4.65 | $4.65 | Mouser
capacitor gate (optional) 4700pF 10 kVolts 2 | $4.84 | $9.68 | Mouser
| capacitor HV (optional) 2500pF 15 kVolts | 1 | $6.16 | $6.16 | Mouser
Fig. 2 | Resistors SMD 1 M Ohm 1/4W 1206 | 58 | $0.23 | $13.34 | Digikey
T. Reinecke, B.H. Clowers / HardwareX 4 (2018) e00030 | 7


5. Operation instructions


Once assembled and tested electrically (i.e. the resistance is appropriate across the voltage divider, grids in the ion shutter are not short circuited, aperture grid is not touching the detector) a high voltage source may be applied to the 1st electrode of the electrode alignment board. Though outside the scope of this hardware description, a high voltage power supply is necessary for the correct operation of the PCB-IMS. With 29 electrodes per 10 cm, the resistor chain for a 20 cm cell is approximately 58 MO which requires 160–200 mA at 10–12 kV to achieve an electric field strength of 500–600 V/cm.
Prior to operation the following checklist should be followed (at a minimum):

Sufficient clearance is provided from other conductive surfaces to avoid high voltage discharge.
Ensure that a source of clean-dry drift gas (e.g. air or nitrogen) is present flowing over the detector at a rate of 200–500 mL/min.
Power is connected to the transimpedance amplifier and the unit is operational.
o Testing of the amplifier can e.g. be performed by applying a voltage of 1 V over a 100 MO at the input (i.e. input current of 109
A) and checking if an output voltage of 1 V can be measured when the amplification is set to ‘‘1e9” and an output voltage of 0.1 V when the amplification is set to ‘‘1e8” respectively.
The resistors comprising the voltage divider are secured and the appropriate resistances are measured between electrodes.
A resistor of approximately 500 kO is placed between the aperture grid and ground.
No electrical connection exists between Grid1 and Grid2 and Grid2 and Grid3.
o Altering the potential of Grid2 is the primary mechanism of modulating the ion beam.
o Operation of the IMS in an open mode can be achieved by placing Grid2 in the resistor chain of the system at the potential midway between Grid1 and Grid3.

Fig. 12. Schematic of the connected aperture grid.

Fig. 13. PCB layout and photo of the high-speed, high-gain transimpedance amplifier.


If possible, limit the current output of the high voltage power supply only to the value needed for safe operation.
o Recognizing that high voltage itself is not necessarily dangerous, extreme caution is advised when using high voltage power supplies capable of delivering such levels of current. Prior to operation, it is advised that those unfamiliar with such hardware contact a subject matter expert or their organization’s electrical safety officer to ensure proper engineering controls are in place.

A range of different ionization sources are compatible with ion mobility spectrometry. On a fundamental level the source of the ions is not as important but the simple fact that ions are produced in a reproducible fashion. Relevant examples include 63Ni [17], 3
H [18], corona discharge [19], micro-plasma [20], electron sources [21], x-rays [22], and electrospray ionization (ESI) [23].
Though radioactive sources are widely deployed, their use requires appropriate safety and licensing and are not recommended unless there is a specific need. For initial experimentation, a corona discharge can be employed. A standard corona source can be made by using any reasonably sharp metal pin located 1 cm from the first electrode and biased 3–4 kV above that entrance potential. As Fig. 15 illustrates, the ion gates may be toggled in an on an off fashion using the electronics referenced previously [13]. It is worth noting that when measuring positive ions using the system the transimpedance amplifier

Fig. 14. Schematic of the of the high-speed, high-gain transimpedance amplifier.


Fig. 15. Measured spectrum for an continuously open and closed ion gate.

T. Reinecke, B.H. Clowers / HardwareX 4 (2018) e00030 | 9

will register a negative voltage and the opposite is true for negative ions. Alternatively, it is simple enough to test whether the system remains in an operational state with respect to measuring ion current simply by turning the ion source on and off while the gate is held open.

6. Validation and characterization

The first ring of the desolvation region was connected to an electric potential of 11.5 kV via a high voltage power supply. To stabilize the drift voltage, an additional capacitor (capacitor HV 2500pF 15 kV) was connected in parallel to the complete IMS system. The drift gas inlet on the detector was connected to a supply of purified nitrogen. The flow rate was set to 0.5 L/min via a mass flow controller (a simple ball meter can also suffice). The detector of the IMS is connected to the amplifier. For data acquisition and generation of the trigger pulse for the pulse generator we used an Analog Discovery (Digilent, Pullman, WA) unit. The pulse width of the injection pulse was set to 50 ms. For the measurement of the corona-ionization spectrum (Fig. 17(a)), a home built corona needle was placed centric and in close proximity to the first ring of the desolvation region and connected to an electric potential of 14.5 kV. Then, sampled headspace from 2,4-lutidine was applied via a PEEK


Fig. 16. Capillary inlet for gaseous samples.


Fig. 17. Representative spectra obtained using the PCB IMS. The top spectrum (a), corresponds to the peaks observed for the headspace from a 2,4-lutidine sample ionized using a corona needle. The lower spectrum (b), corresponds to a series of tetraalkylammonium salts electrosprayed at room temperature. The resolving powers (i.e. peak centroid divided by peak width at half height) for the two spectra range from R = 82 (Corona spectrum) to R = 92 (ESI spectrum).

capillary which is connected to a gas tight syringe containing the sample. The capillary sample inlet is shown in Fig. 16. The assembly is similar to the assembly of the drift gas inlet described above, while using a 0.01 ID/0.062 OD PEEK capillary instead of the Teflon hose. Due to the smaller diameter of the capillary compared to the Teflon hose, only one (middle) of the three spacers used has a cut out. It should be noted that a range of gas-phase sample introduction mechanisms may be implemented.
For the measurement of the ESI spectrum (Fig. 17(b)), the corona needle was replaced by an ESI needle which was then connected to a potential of 13.5 kV. A 12 mM solution of a series of tetraalkylammonium salts was then supplied with a syringe pump and a flow rate of 5 mL/min. The resolving powers (i.e. peak centroid divided by peak width at half height) for the two spectra range from R = 82 (Corona spectrum) to R = 92 (ESI spectrum).

Declaration of interest

B.H. Clowers is a co-inventor of a number of patents (US-2009294662-A1, US-2007158543-A1, US-2013260478-A1, US-2017074826-A1, US-2017023453-A1) related to ion mobility spectrometry, however, the present report does not infringe on those disclosures.

Acknowledgement

We would like to acknowledge support from the NSF under award CHE-1506672.

Appendix A. Supplementary data

Supplementary data associated with this article can be found, in the online version, at https://doi.org/10.1016/j.ohx.2018. e00030. (https://doi.org/10.1016/j.ohx.2018.e00030)

References

[1] G.A. Eiceman, Z. Karpas, H.H. Hill Jr., Ion Mobility Spectrometry, third ed. (http://refhub.elsevier.com/S2468-0672(18)30029-4/h0005), CRC Press, 2013. (http://refhub.elsevier.com/S2468-0672(18)30029-4/h0005)
[2] X. Zhang, K. Quinn, C. Cruickshank-Quinn, R. Reisdorph, N. Reisdorph, The application of ion mobility mass spectrometry to metabolomics, Curr. Opin. Chem. Biol. 42 (2018) 60–66. (http://refhub.elsevier.com/S2468-0672(18)30029-4/h0010)
[3] I.D.G. Campuzano, J.L. Lippens, Ion mobility in the pharmaceutical industry: an established biophysical technique or still Niche?, Curr Opin. Chem. Biol. 42 (2018) 147–159. (http://refhub.elsevier.com/S2468-0672(18)30029-4/h0015)
[4] K.A. Morrison, B.H. Clowers, Contemporary glycomic approaches using ion mobility–mass spectrometry, Curr. Opin. Chem. Biol. 42 (2018) 119–129. (http://refhub.elsevier.com/S2468-0672(18)30029-4/h0020)
[5] R.G. Ewing, D.A. Atkinson, G.A. Eiceman, G.J. Ewing, A critical review of ion mobility spectrometry for the detection of explosives and explosive related compounds, Talanta 54 (3) (2001) 515–529. (http://refhub.elsevier.com/S2468-0672(18)30029-4/h0025)
[6] M.A. Mäkinen, O.A. Anttalainen, M.E.T. Sillanpää, Ion mobility spectrometry and its applications in detection of chemical warfare agents, Anal. Chem. 82 (23) (2010) 9594–9600. (http://refhub.elsevier.com/S2468-0672(18)30029-4/h0030)
[7] S. Kim, R.P. Rodgers, A.G. Marshall, Truly, ‘‘exact” (http://refhub.elsevier.com/S2468-0672(18)30029-4/h0035) mass: elemental composition can be determined uniquely from molecular mass measurement at (http://refhub.elsevier.com/S2468-0672(18)30029-4/h0035) 0.1mda accuracy for molecules up to (http://refhub.elsevier.com/S2468-0672(18)30029-4/h0035) 500Da, Int. J. Mass Spectrom. 251 (2–3) (2006) 260–265. (http://refhub.elsevier.com/S2468-0672(18)30029-4/h0035)
[8] K. Giles, E.P. Grimsrud, The kinetic ion mobility mass spectrometer: measurements of ion-molecule reaction rate constants at atmospheric pressure, J. Phys. Chem. 96 (16) (1992) 6680–6687. (http://refhub.elsevier.com/S2468-0672(18)30029-4/h0040)
[9] P. Kwantwi-Barima, H. Ouyang, C.J. Hogan, B.H. Clowers, Tuning mobility separation factors of chemical warfare agent degradation products via selective ion-neutral clustering, Anal. Chem. 89 (22) (2017) 12416–12424. (http://refhub.elsevier.com/S2468-0672(18)30029-4/h0045)
[10] H.E. Revercomb, E.A. Mason, Theory of plasma chromatography/gaseous electrophoresis. Review, Anal. Chem. 47 (7) (1975) 970–983. (http://refhub.elsevier.com/S2468-0672(18)30029-4/h0050)
[11] A.T. Kirk, S. Zimmermann, Bradbury-Nielsen vs. field switching shutters for high resolution drift tube ion mobility spectrometers, Int. J. Ion Mobil. Spec. 17 (3-4) (2014) 131–137. (http://refhub.elsevier.com/S2468-0672(18)30029-4/h0055)
[12] A. Bohnhorst, A.T. Kirk, S. Zimmermann, Simulation aided design of a low cost ion mobility spectrometer based on printed circuit boards, Int. J. Ion Mobil. Spectrom. 19 (2–3) (2016) 167–174. (http://refhub.elsevier.com/S2468-0672(18)30029-4/h0060)
[13] L. Garcia, C. Saba, G. Manocchio, G.A. Anderson, E. Davis, B.H. Clowers, An open source ion gate pulser for ion mobility spectrometry, Int. J. Ion Mobil. Spectrom. 20 (3–4) (2017) 87–93. (http://refhub.elsevier.com/S2468-0672(18)30029-4/h0065)
[14] T. Reinecke, A.T. Kirk, A. Ahrens, C.-R. Raddatz, C. Thoben, S. Zimmermann, A compact high resolution electrospray ionization ion mobility spectrometer, Talanta 150 (2016) 1–6. (http://refhub.elsevier.com/S2468-0672(18)30029-4/h0070)
[15] Y. Du, H. Cang, W. Wang, F. Han, C. Chen, L. Li, K. Hou, H. Li, Note: design and construction of a simple and reliable printed circuit board-substrate bradbury-nielsen gate for ion mobility spectrometry, Rev. Sci. Instrum. 82 (8) (2011) 086103. (http://refhub.elsevier.com/S2468-0672(18)30029-4/h0075)
[16] J. Langejuergen, M. Allers, J. Oermann, A. Kirk, S. Zimmermann, High kinetic energy ion mobility spectrometer: quantitative analysis of gas mixtures with ion mobility spectrometry, Anal. Chem. 86 (14) (2014) 7023–7032. (http://refhub.elsevier.com/S2468-0672(18)30029-4/h0080)
[17] C.L. Crawford, H.H. Hill, Comparison of reactant and analyte ions for 63nickel, corona discharge, and secondary electrospray ionization sources with ion mobility-mass spectrometry, Talanta 107 (2013) 225–232. (http://refhub.elsevier.com/S2468-0672(18)30029-4/h0085)
[18] A.T. Kirk, M. Allers, P. Cochems, J. Langejuergen, S. Zimmermann, A compact high resolution ion mobility spectrometer for fast trace gas analysis, Analyst 138 (18) (2013) 5200–5207. (http://refhub.elsevier.com/S2468-0672(18)30029-4/h0090)
[19] H. Borsdorf, H. Schelhorn, J. Flachowsky, H.-R. Döring, J. Stach, Corona discharge ion mobility spectrometry of aliphatic and aromatic hydrocarbons, Anal. Chim. Acta 403 (1–2) (2000) 235–242. (http://refhub.elsevier.com/S2468-0672(18)30029-4/h0095)
[20] W. Vautz, A. Michels, J. Franzke, Micro-plasma: a novel ionisation source for ion mobility spectrometry, Anal. Bioanal. Chem. 391 (7) (2008) 2609– 2615. (http://refhub.elsevier.com/S2468-0672(18)30029-4/h0100)
[21] P. Cochems, M. Runge, S. Zimmermann, A current controlled miniaturized non-radioactive electron emitter for atmospheric pressure chemical ionization based on thermionic emission, Sens. Actuat. A Phys. 206 (2014) 165–170. (http://refhub.elsevier.com/S2468-0672(18)30029-4/h0105)
[22] T. Reinecke, A.T. Kirk, A. Heptner, D. Niebuhr, S. Böttger, S. Zimmermann, A compact high-resolution X-ray ion mobility spectrometer, Rev. Sci. Instrum. 87 (5) (2016) 053120. (http://refhub.elsevier.com/S2468-0672(18)30029-4/h0110)
[23] C. Wu, W.F. Siems, G.R. Asbury, H.H. Hill, Electrospray ionization high-resolution ion mobility spectrometry-mass spectrometry, Anal. Chem. 70 (23) (1998) 4929–4938. (http://refhub.elsevier.com/S2468-0672(18)30029-4/h0115)
T. Reinecke, B.H. Clowers / HardwareX 4 (2018) e00030 | 11

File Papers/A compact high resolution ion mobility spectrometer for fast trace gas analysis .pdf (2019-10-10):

# Analyst

ISSN 0003-2654; www.rsc.org/analyst; Volume 138 | Number 18 | 21 September 2013 | Pages 5159–5504

Title of Themed Issue to go here - bar colour to contrast OFC image

HOT PAPER
Ansgar T. Kirk et al.
A compact high resolution ion mobility spectrometer for fast trace gas analysis

### A compact high resolution ion mobility spectrometer for

### fast trace gas analysis

Ansgar T. Kirk,* Maria Allers, Philipp Cochems, Jens Langejuergen
and Stefan Zimmermann

Drift tube ion mobility spectrometers (IMS) are widely used for fast trace gas detection in air, but portable compact systems are typically very limited in their resolving power. Decreasing the initial ion packet width improves the resolution, but is generally associated with a reduced signal-to-noise-ratio (SNR) due to the lower number of ions injected into the drift region. In this paper, we present a refined theory of IMS operation which employs a combined approach for the analysis of the ion drift and the subsequent amplification to predict both the resolution and the SNR of the measured ion current peak. This theoretical analysis shows that the SNR is not a function of the initial ion packet width, meaning that compact drift tube IMS with both very high resolution and extremely low limits of detection can be designed. Based on these implications, an optimized combination of a compact drift tube with a length of just 10 cm and a transimpedance amplifier has been constructed with a resolution of 183 measured for the positive reactant ion peak (RIP⁺

), which is sufficient to e.g. separate the RIP⁺ from the protonated acetone monomer, even though their drift times only differ by a factor of 1.007. Furthermore, the limits of detection (LODs) for acetone are 180 pptv within 1 s of averaging time and 580 pptv within only 100 ms.

Introduction

Dri tube ion mobility spectrometers (IMS) characterize different substances by ionizing analytes and studying the motion of the ions through a so-called dri gas under the inuence of an electric eld. IMS have earned a reputation for providing extremely good detection limits in the low ppb- and even ppt-range in a short period of time, usually in less than a second, and at relatively low cost.¹,2 These advantages have led to their widespread use as fast detectors for explosives, drugs, chemical warfare agents, or other hazardous substances.³,4 In the past years, many other applications in science and industry have been explored. Examples are bioanalysis,⁵⁻⁷ quality control for food,⁸,9 and medication¹⁰,11 or polymer characterisation.¹² However, ion mobility spectrometers are limited in their applications as they are generally considered as low-resolution devices. Typical products that are commercially available achieve resolutions dened as the ratio of the dri time tD and the full width at half maximum (FWHM) of 20–60.¹³ This can lead to unwanted false negatives or positives as the measurement uncertainty for a peak position may be too high to obtain an unambiguous identication. Furthermore, small peaks may be masked by larger peaks of similar mobilities or the sum of two peaks of similar height may appear as a single peak of intermediate mobility.
Therefore, the improvement of the analytical performance of IMS both through operational and instrumental developments has been an ongoing task over the past decades. Operational improvements may include techniques such as post-processing of the acquired spectra to separate conjoined peaks,¹⁴ sweeping of the dri voltage for dri tubes with a mobility dependent separation performance,¹⁵ or using ion–ion recombination dynamics as an orthogonal pre-separation method.¹⁶ However, such techniques are always limited by the overall performance of the dri tube itself.
The typical instrumental approach to achieve higher resolution is the construction of longer dri tubes, mainly used in IMS-MS applications. These large laboratory devices can reach a signicantly higher resolution than commercial instruments. Values of 172 for single-charged¹⁷ and 240 for multiple charged ions,¹⁸ which are typically easier to separate, have been reported for a 63 cm long dri tube. For multiple charged ions, the so-called ion cyclotron ion mobility spectrometer, which uses a circular dri tube with a length of about 180 cm to prolong the ion ight as long as ion storage is possible,¹⁹ has achieved resolutions up to 400. It however acts as an ion lter and therefore sweeping different cycle frequencies is required to measure the whole spectrum. In addition to this, signal intensities are low due to heavy ion losses,²⁰ leading to long acquisition times. All these devices have dimensions too large for

Leibniz University Hannover Institute of Electrical Engineering and Measurement Technology, Dept. of Sensors and Measurement Technology, Appelstr. 9A, 30167 Hannover, Germany. E-mail: kirk@geml.uni-hannover.de; Tel: +49 511 762 4672

Cite this: Analyst, 2013, 138, 5200

Received 31st January 2013 Accepted 19th April 2013

DOI: 10.1039/c3an00231d

www.rsc.org/analyst

5200 | Analyst, 2013, 138, 5200–5207 | This journal is ª The Royal Society of Chemistry 2013
Open Access Article. Published on 23 April 2013. Downloaded on 10/10/2019 5:06:52 PM. This article is licensed under a Creative Commons Attribution-NonCommercial 3.0 Unported Licence. View Article Online View Journal | View Issue

portable instruments. Furthermore, such laboratory systems have higher manufacturing cost limiting widespread eld use. A compromise between the current commercial designs and much larger laboratory prototypes is available in the form of a 26 cm long resistive glass tube design.²¹ This ion mobility spectrometer was reported to reach resolutions between 60 and 150, primarily depending upon the used ion source.
Here we present a rened theory of IMS operation that allows us to design compact dri tube IMS with both very high resolution and extremely low limits of detection. Based on this theory, a 10 cm short dri tube IMS with a resolution of 183 – measured for the positive reactant ion peak (RIP⁺
) – and limits
of detection within the low pptv-range has been developed. Furthermore, with multi-physics simulations a good understanding of the ions' motion inside the dri tube has been developed over the past few years.²²,23 With such tools at hand, it seems possible to further optimize our IMS to reach resolutions above 200.

Theoretical section

Basic theory

In order to understand how the construction of a compact high resolution IMS can be possible, it is rst necessary to recognize which factors determine the resolution of a dri tube and how they interact with each other. For this purpose, a known analytical model of the measurement process in an ion mobility spectrometer is used. It is assumed that, at a certain point in time, an ion packet with Gaussian shape and an initial temporal width wInj is injected into the dri region. The distance to the detector is dened as the dri length L and the voltage applied across is the dri voltage UD. The ions travel with a dri velocity proportional to their ion mobility K and undergo broadening by diffusion, which is described using the absolute temperature T, Boltzmann's constant kB and the elementary charge e. The quality of the achieved separation is usually expressed by the resolution R, which is dened as the ratio of the dri time tD and the full width at half maximum (FWHM) upon arrival at the detector. In the following we dene w0,5 ¼ FWHM. Using the well-known terms for tD and w0,5,

24 eqn (1) can be derived. This equation has been extensively used in the past to analyse the resolution of IMS.²⁵

R ¼ tD

w0;5

¼

L²
KUD ffiffiffiffiffiffiffiffiffiffiffiffiffiffiffiffiffiffiffiffiffiffiffiffiffiffiffiffiffiffiffiffiffiffiffiffiffiffiffiffiffiffiffiffiffiffiffiffiffiffiffiffiffiffiffiffiffiffiffiffi

wInj

2
þ

16 kB T ln 2
e UD

L²

KUD

2 s | (1)

It is obvious that eqn (1) must reach a maximum at a certain dri voltage, as the resolution decreases due to the increasing peak broadening by diffusion at lower dri voltages and the increasing inuence of the initial temporal width of the ion packet at higher dri voltages. By calculating the partial derivative of eqn (1) with respect to UD, eqn (2) can be found. It species the optimum voltage Uopt, at which the said resolution maximum is reached. Substituting this result into eqn (1) yields eqn (3), which describes the maximum achievable resolution

Ropt for a certain dri tube IMS. Using this quantity for further analysis instead of eqn (1) simplies calculations and allows a better understanding of the complex interactions between the different other parameters affecting the resolution.

Uopt ¼

ffiffiffiffiffiffiffiffiffiffiffiffiffiffiffiffiffiffiffiffiffiffiffiffiffiffiffiffiffiffiffiffiffiffiffi
8kB T ln 2
e K²

L⁴

wInj

2

3

s
(2)

Ropt ¼

ffiffiffiffiffiffiffiffiffiffiffiffiffiffiffiffiffiffiffiffiffiffiffiffiffiffiffiffiffiffiffiffiffiffiffiffiffiffiffiffiffiffiffiffiffiffiffiffi
e

# 24 ffiffiffi

3

p ln 2 kB TK

L²

wInj

3

s

(3)

For constant operating conditions, the achievable resolution is only determined by the ratio of L²
/wInj. Therefore, the resolution can be kept constant even for short dri tube lengths as long as sufficiently small ion packets are injected.
Increasing the dri length to achieve higher resolution is of course much easier, but contradicts our goal of compact IMS. The required voltage to achieve a certain resolution is proportional to its square, independent of the length of the dri tube, as Ropt depends on L²

/wInj and Uopt depends on L⁴
/wInj2
. Thus,
high resolution IMS will always require high dri voltages. It should be also noted that the temporal ion packet width at the detector is directly proportional to the initial temporal ion packet width if the optimum dri voltage is applied. This relationship can be derived by evaluating the denominator of eqn (1) for the voltage specied by eqn (2). The result is given in eqn (4), which is extremely helpful, as it facilitates many of the following calculations.

# w0;5ðUD ¼ UoptÞ¼ ffiffiffi

3

p wInj | (4)

Amplier, ion loss, and SNR

Although the present model offers a useful and accurate prediction for the processes inside an ion mobility spectrometer, it suffers from two shortcomings. First, no equation to analyse the signal-to-noise-ratio is integrated into the model. Second, the resolution is predicted for the ion current peak at the detector, but the measured signal is the output voltage aer amplication. Usually the equivalent input noise generated by the high-gain transimpedance ampliers used in IMS applications is inversely proportional to their rise time,²⁶ meaning that a compromise between these quantities is necessary. Thus, it can be expected that the amplier signicantly inuences both the resolution and the signal-to-noise-ratio of the instrument. Consequently, the present model for evaluating the IMS resolution must be extended to include the effects of a non-ideal amplier. The frequency spectrum of a Gaussian peak is given by eqn (5) and is a Gaussian peak itself, with a standard deviation proportional to the temporal half width w0,5. Fourier transform was carried out using the frequency f. Multiplying the peak's frequency spectrum with the amplier's transfer function leads to the output spectrum, which can be transformed back to the time domain, where peak distortion becomes visible.²⁷ Calculating the resulting distortion this way is possible, but not feasible, since it cannot be expressed by a simple equation to be integrated into an applicable model for predicting resolution and SNR.

This journal is ª The Royal Society of Chemistry 2013 | Analyst, 2013, 138, 5200–5207 | 5201
Paper | Analyst

Open Access Article. Published on 23 April 2013. Downloaded on 10/10/2019 5:06:52 PM. This article is licensed under a Creative Commons Attribution-NonCommercial 3.0 Unported Licence. View Article Online


FðfÞ¼ w0;5
2

## ffiffiffiffiffiffiffi

p

ln2 r
e-

p2f 2w0;5

2
4 ln 2 | (5)

However, a relationship which can be used to derive a useful approximation for the peak distortion and its effect on resolution is shown in Fig. 1. Here, the resolution aer amplication by a non-ideal amplier is compared to that resulting from a longer initial pulse width.
Close to the resolution maximum, the agreement between the two curves is excellent. It should be noted that this similarity exists for all stable ampliers. Therefore it is possible to transfer eqn (1)–(4) to a renedmodel by replacing the initial temporal ion packet width wInj with a longer temporal width also accounting for the amplier. wInj should still be used whenever an effect directly related to the injection, like ion loss at the shutter grid, is analysed. Therefore, we dene a minimum temporal width wMin, as it represents the minimum temporal half width at the detector that a certain dri tube–amplier combination can achieve. When combining different contributors to the width of a Gaussian peak, as for example the initial width wInj and the diffusion term in the denominator of eqn (1), geometric addition is used. Therefore, wMin is dened by eqn (6) as the geometric addition of wInj and the additional quantity wAmp, which describes the inuence of the amplier.

wMin ¼

# ffiffiffiffiffiffiffiffiffiffiffiffiffiffiffiffiffiffiffiffiffiffiffiffiffiffiffi

wInj2 þ wAmp2

q
(6)

For calculating wMin from readily available data, it is necessary to express wAmp in terms of a measurable property of the transimpedance amplier. As the frequency response is too complex to derive a direct relationship, the rise time tr 10–90 was chosen. Using simulations, a large number of different combinations of ampliers and initial ion packet widths were analysed. For each combination, the exact resolutions aer amplication were calculated numerically for several dri voltages and a least-squares-t was applied to determine the respective value of wAmp which results in the smallest deviation between the exact results and those approximated using eqn (6). As shown in Fig. 2, the necessary value of wAmp is nearly proportional to the rise time of the amplier and therefore inversely proportional to its noise sNoise, yielding eqn (7) and (8). These relationships can be used to simplify the analysis of resolution and signal-to-noise-ratio for the complete system including the dri tube and transimpedance amplier.

wAmp ¼ 0.9tr 10-
90 | (7)

sNoise e

1

wAmp

(8)

The fact that the additional broadening is lower than the rise time of the amplier can be attributed to the Gaussian shape of the peak. The spread between the resulting values of wAmp for a single value of tr 10-90 in Fig. 2 is caused by the fact that the rise time alone cannot attribute for all the subtleties of the frequency response.
Knowing the half-width at the detector and the noise, the only missing quantity for calculating the signal-to-noise-ratio is the peak area or total charge Q. It is determined from the amount of charge injected into the dri tube and the subsequent ion losses during the dri. As the dri time scales proportional to L²
, when
a constant dri voltage is applied, no signicant radial diffusion is expected to occur inside a compact dri tube. Therefore, the charge at the detector should be similar to the injected amount of charge. This assumption corresponds well with simulation results.²³ For the calculation of the injected charge, it should be noted that our dri tube design is not based on a Bradbury– Nielsen-shutter, but switches a high dri eld inside the ionization region for ion packet injection. As the transparency of the grid to ions strongly depends on the ratio of the electric drield strength and the injection eld strength,²⁸ the number of ions injected through such a shutter will increase proportionally to the dri eld. Furthermore, the shorter and higher the pulse to reach a minimum initial ion packet width, the lower the number of ions injected. Taking into account that shorter dri times allow for higher number of averages n at the same time, the SNR can be estimated by eqn (9), with Q/w0,5 representing the peak height and sNoise= ffiffiffi

n p representing the remaining noise aer

averaging. The charge Q is determined by the eld-dependant injection ion loss as described before and is therefore proportional to wInj ED, while the number of averages n is inversely proportional to the dri time tD.

SNR Q

w0;5

ffiffiffi

n p

sNoise

wInj ED

w0;5 sNoise

ffiffiffiffiffi
tD
p | (9)

Using the relationships between the different factors, which are known from eqn (1)–(4) and (8) and the fact that tD L/ED, eqn (9) can be simplied to eqn (10). It is interesting to note that


Fig. 1 Resolutions for wInj ¼ 10 ms (solid line), wInj ¼ 14 ms (dashed line) and wInj ¼ 10 ms filtered by a PT1 with fg ¼ 32 kHz (circles).

Fig. 2 Relationship between wAmp and tr 10–90 obtained from a simulation. Error bars indicate standard deviation. The solid line represents a linear least-squares-fit.

5202 | Analyst, 2013, 138, 5200–5207 | This journal is ª The Royal Society of Chemistry 2013
Analyst | Paper

Open Access Article. Published on 23 April 2013. Downloaded on 10/10/2019 5:06:52 PM. This article is licensed under a Creative Commons Attribution-NonCommercial 3.0 Unported Licence. View Article Online


there is no direct inuence of the dri length on the SNR, as the effects of changing eld strengths and averaging compensate each other.

SNR wInj wAmp

wMin

# ffiffiffiffiffiffiffiffi

ED3
L

s

wInj wAmp
wInj 2 þ wAmp 2 | (10)

The normalised resolutions and SNR calculated using eqn (3), (6) and (10) for different ratios wInj/wAmp are plotted in Fig. 3. In order to achieve the maximum SNR, both widths should be chosen to be identical. The maximum resolution for a given temporal width is achieved, when the contribution of the other width becomes negligible. This however should not be misinterpreted, as it also means that only a fraction of the maximum possible resolution related to the shorter width will be obtained. When the resolution is normalized to the maximum possible resolution related to the shorter width, it becomes obvious that the best resolution efficiency is also reached for equal widths. Interestingly, a reduction of the initial width can lead to an increase of the SNR, as the IMS is shied to a more favourable operating point. In addition, equal temporal widths will cause the SNR to remain constant for all possible values. Thus, the SNR is independent from the initial ion packet width. In other words, the initial ion packet width can be reduced without loss of detection limit or increasing measurement time. This is an extremely important observation, as it provides the basis for the construction of a compact high resolution ion mobility spectrometer without sacricing the excellent limits of detection.
To demonstrate the above ndings, a peak of an ion mobility spectrometer with a resolution of 60 and a SNR of 50 is shown in panel (A) of Fig. 4. Aiming at improving this resolution above 180 by the presented approach, both the initial ion packet width wInj and the amplier width wAmp, which corresponds to the amplier rise time tr 10-90, must be reduced by a factor of 27 according to eqn (3) and (6). At the same time, the applied dri voltage and therefore the electric dri eld are increased by a factor of 9 according to eqn (2). The increased dri eld strength results in both proportionally less ion loss upon ion packet injection and shorter dri times allowing for more averages at the same time, thus mitigating the negative effects of the reduced widths. In fact, the charge injected into the dri tube will decrease by a factor of 27/9 ¼ 3 and the standard deviation of the noise will increase by a factor of 27= ffiffiffi

9 p ¼ 9,

thus resulting in a total decrease of the SNR by a factor of 27. However, according to eqn (4), the temporal half width at the detector will also decrease by a factor of 27, which in turn increases the SNR by a factor of 27. As these three effects compensate each other, the SNR remains constant as shown in panel (B) of Fig. 4. Despite the increased noise and the reduced amount of charge reaching the detector, the taller peak results in a constant SNR.

Scaling rules

Based on the predictions of the extended model, both very high resolution and excellent limits of detection can be achieved in a compact IMS at the same time. However, miniaturization and subsequent scaling of parameters give rise to other factors, which are negligible in longer dri tube designs. Thus, these phenomena must be evaluated in order to achieve the desired high resolution. To do so, the relationships presented in Table 1 can be easily derived from eqn (1)–(4). They present a useful guideline on how conditions inside the dri tube will change when ion mobility spectrometers are scaled down to a size suitable for portable instruments while keeping the resolution constant.

Field inhomogeneities

A well-known problem in dri tube designs is the negative effect of dri eld inhomogeneities on the resolution and, due to the constant amount of charge, also signal intensity. Eqn (11) describes a simple model for eld inhomogeneities: Two ions of


Fig. 3 Normalized SNR (dotted) and resolution normalized to the maximum resolution possible based on the amplifier width (dashed) or related to the shorter of the two widths (solid).

Fig. 4 Peaks for different measurement parameters. Both panels show a 2 ms wide excerpt from the respective spectra. In (B) the initial ion packet and amplifier widths have been reduced by a factor of 27 compared to (A), and the voltage has been readjusted according to eqn (2).

Table 1 Relationships for size-scaling of a drift tube at constant resolution

Quantity | Symbol | Scaling
Injection width | wInj | L²
FWHM at the detector | w0,5 | L²
Electric dri eld strength | ED | L-
| | 1
Dri voltage | UD | Not required
Dri time | tD | L²
This journal is ª The Royal Society of Chemistry 2013 | Analyst, 2013, 138, 5200–5207 | 5203

Open Access Article. Published on 23 April 2013. Downloaded on 10/10/2019 5:06:52 PM. This article is licensed under a Creative Commons Attribution-NonCommercial 3.0 Unported Licence. View Article Online the same mobility travel from one equipotential line to another, traversing the distance l and the voltageEDl. Prolonging one of the ight paths by Dl results in a relative peak broadening DtD/w0,5.

DtD

w0;5

# ¼ ðl þ DlÞ

2
KEDlw0;5

l

2
KEDlw0;5

z 2Dl
KEDw0;5

0

R ¼ const

¹
L (11)

This indicates the following. When a dri tube is scaled down and a constant specied resolution is demanded, the effect of eld inhomogeneities will grow inversely proportional to the dri length. We used multi-physics simulations to evaluate different dri tube geometries and to nd an optimum design.

Mirror charges

The electric eld of an ion packet traveling inside the dri tube will induce a mirror charge of opposite polarity on any metal surface, including the detector. This causes charges to gradually ow onto the Faraday plate as the ions move closer, thus broadening the peak. To prevent this, a so-called aperture grid is usually placed in front of the detector to shield the detector from the electric eld. This grid however does not provide perfect shielding, as it is neither a continuous metal surface nor innitely close to the detector. As the width of the ion packet decreases in proportion to the square of the reduced dri lengths, the shielding must be improved likewise to prevent negative effects on the resolution. This can be accomplished by moving the Faraday plate closer to the aperture grid or increasing the voltage between the detector and the aperture grid in order to minimize the time ions spend in this unshielded region. Another possible approach is decreasing the mesh size of the grid to minimize eld penetration. Unfortunately, all of these changes also increase the susceptibility of the device to mechanical vibrations, requiring a mechanically more stable construction of the detector unit.

Coulomb repulsion

Mutual Coulomb repulsion between the ions of a moving ion packet can lead to further broadening and loss of resolution. While the associated equations are too complex to nd an exact analytical solution, a good approximation is possible by applying Gauss' law to the charge cloud, assuming a symmetrical distribution.²⁹ Based on this, the force exerted on the cloud's surface and its resulting displacement over time can be calculated. In our design, a radioactive tritium source with a diameter of 10 mm is employed to minimize the charge density while maintaining a high absolute charge. Due to the large ionization area and the short initial peak width, the ion cloud can be well approximated by an innitely thin disk. Gauss' law then yields a constant eld EIon in eqn (12) throughout the dri, which only depends on the ratio of total charge Q to surface area A and the free space permittivity 30.

EIon ¼ Q
2A30

(12)

Decreasing the amount of travelling charge and increasing the dri velocity vD both lead to a reduction of the spatial displacement, resulting in a lower relative temporal half width Dw0,5/w0,5 caused by Coulomb repulsion, as shown in eqn (13).

Dw0;5

w0;5

KEIontD

w0;5vD

0

R ¼ const
L² | (13)

Coulomb repulsion should therefore be less critical when scaling down ion mobility spectrometers while keeping the resolution constant. This effect could also promote ionization sources with adjustable intensity, like corona discharge,²⁸,30 or non-radioactive electron emitters,³¹ to achieve higher signal intensities and therefore lower limits of detection.

High eld effects and breakdown

Finally, high-eld effects have to be considered, which are eld dependent ion mobilities leading to dri velocities not directly proportional to the electric eld strength, and the possibility of a gas discharge. Both effects become increasingly important when miniaturizing IMS due to growing eld strengths. The high-eld region is expected at voltages high enough to gain energy from the electric eld comparable to the thermal energy of an ion. Estimations in the literature are sometimes as low as 2 Td,² but in FAIMS usually no measurable changes in mobility could be observed below 10 Td.³²,33 For operating conditions of 1013 mbar and 298.15 K, this would result in electric eld strengths between 50 V mm-

1 and 250 V mm-
1 | . Such electric
elds are possible in compact IMS, so that high-eld effects on the ion mobility need to be considered. Both values are signicantly lower than the eld strengths required for a gas
discharge, which is estimated to be 3000 V mm- | 1 for the
mentioned operating conditions. However, certain metal parts, particularly the guard rings, are usually separated by smaller gaps than the corresponding dri length inside the dri tube, resulting in accordingly higher local eld strengths. Therefore the Paschen curve has to be considered upon designing the dri tube to ensure that all gaps are either small or large enough.

Experimental section

IMS design

Based on the considerations presented in the theoretical section of this paper, a compact high resolution dri tube was constructed. The basic layout is similar to typical dri tube designs, consisting of an ionization region, a dri region and a shielded Faraday plate as the ion detector. A schematic of our setup is shown in Fig. 5 and its operating parameters are summarized in Table 2. Reactant ion generation is initiated by electron emission from a radioactive H3-source. A metallic grid divides the ionization region from the dri region and ion injection is controlled by pulsing the dri eld inside the ionization region. A resistive voltage divider is used for applying the dri eld. The whole instrument is sealed inside a surrounding PEEK tube, which prevents contamination and directs the ow of the dri gas. Puried air is used as the sample carrier and dri gas.

5204 | Analyst, 2013, 138, 5200–5207 | This journal is ª The Royal Society of Chemistry 2013
Analyst | Paper

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


The sample gas is directly introduced into the ionization region, while the dri gas enters the dri tube from the detector.

Control electronics

Operating a high resolution IMS requires special electronic components with corresponding performance and oen very specic features. The two most important electronic devices are the high voltage pulse generator for ion injection and the transimpedance amplier for ion detection. In order to comply with the specications presented, we developed the electronics as required for high resolution IMS. The high voltage switch offers a rise time of just 100 ns for a 2.2 kV pulse and is able to isolate voltages of up to 25 kV against ground. The transimpedance amplier has a rise time of 5.8 ms and is equipped with special suppression circuitry to minimize the effect of fast high voltage pulses on the measurement signal. High voltage for both the dri and the injection eld was generated by power supplies from FuG. An Agilent MSO9404A oscilloscope was used to record the spectra.

Chemicals and preparation

Acetone used in the measurements as the analyte was purchased from Sigma Aldrich. A permeation oven containing an acetone permeation tube set to 35 C with a constant ow of 600 mls min-1 of puried dry air was used to generate a constant acetone vapour concentration. An adjustable fraction of this gas was diluted with dried and/or humidied air to achieve the desired acetone concentration and humidity in the sample gas.

Results and discussion

In order to verify the theoretical considerations presented in this paper, the maximum resolution achievable for different initial ion packet widths was determined. This was done by sweeping the dri voltage and comparing the obtained resolution. For the optimum dri voltage, the signal-to-noise-ratio was also measured. The results are plotted in Fig. 6 together with curves calculated from eqn (3), (6) and (10), which show excellent agreement with the measured data. In particular the increasing signal-to-noise-ratio for shorter injected ion packets has been veried. This effect allows extremely low detection limits even for very short initial ion packet widths required to achieve high resolutions in compact dri tubes. As the measured SNR reaches its maximum close to the minimum initial width reached in our current setup, it is also shown that the amplier is correctly designed to achieve maximum resolution and detection limit efficiency.
The measured resolutions and ion mobility of the reactant ion peak for different dri voltages are shown in Fig. 7. The error bars indicate a 95% condence interval calculated from

Fig. 5 Schematic diagram of the drift tube.

Table 2 IMS operating parameters

Parameter | Value
Dri length | 98 mm
Dri region diameter | 15 mm
Source diameter | 10 mm
Source activity | 300 MBq
Injection voltage | 250.2000 V
Injection time | 5.350 ms
Repetition rate | 44 Hz
Dri voltage | 4.18 kV
Aperture voltage | 100 V
Dri gas ow | 250 mls min-
| 1
Sample gas ow | 5 mls min-
| 1
Dew point dri gas and
sample carrier

82 C (0.4 ppmv water
vapour concentration)
Operating pressure | 1018 mbar
Operating temperature | 25 C


Fig. | 7 Measured resolution (triangles) and ion mobility (squares). Error bars
indicate 95% confidence interval.

Fig. 6 Measured (dots) and calculated (lines) normalized values of the signal-tonoise-ratio (dashed line, circles) and the resolution (solid line, squares).

This journal is ª The Royal Society of Chemistry 2013 | Analyst, 2013, 138, 5200–5207 | 5205

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


the t-distribution. Since the observed ion mobility is independent of the applied dri voltage, we do not need to consider any high-eld effect in our dri tube.
Fig. 8 shows the ion mobility spectrum of the reactant ion peak for a dri voltage of 13 kV. The resolution is 182.6 0.5 (95% condence interval). Thus, compact ion mobility spectrometers can not only compete with large laboratory dri tube IMS, but even surpass their performance. We suggest reporting a condence interval for the resolution,³⁴ as a single spectrum can reach a much higher apparent resolution due to the noise.

For example, a resolution as high as 205 could be reported for our system. As mentioned, this value does not represent the actual resolution.
In order to demonstrate the resolving power, Fig. 9 shows two spectra acquired for a sample gas containing 20 ppbv acetone. Under our operating conditions the protonated acetone monomer's dri time relative to the RIP⁺ is just 1.007. While the protonated acetone monomer peak is clearly visible in the spectrum with a high resolution of 183, the spectrum with a resolution of 60 does not reveal the presence of a second

Fig. 8 Measured ion mobility spectrum for wInj ¼ 5 ms and UD ¼ 13 kV. The inset shows the measured RIP⁺ with R ¼ 183.


Fig. 9 Measured spectra of 20 ppbv acetone at two different resolutions. A resolution of 60 (dotted line) is insufficient to resolve the two peaks visible at a resolution of 183 (solid line).

5206 | Analyst, 2013, 138, 5200–5207 | This journal is ª The Royal Society of Chemistry 2013
Analyst | Paper

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

peak close to the RIP⁺
. The increased resolution therefore provides superior information and hence superior potential for chemical analysis. It should be noted that the same amplier was used for both spectra shown in Fig. 9.
The limits of detection for acetone have been determined for averaging times of 100 ms (4 averaging) and 1 s (44 averaging). Using three times the standard deviation of the respective noise, the resulting LODs are 580 pptv and 180 pptv.

Conclusions

The viability of both the presented theoretical design approach and the compact high resolution ionmobility spectrometerwith a resolution of 183 has been demonstrated. Combining the compact size suitable for portable instruments with limits of detection in the low pptv range and a resolution that surpasses large dri tubes used in lab experiments, this device can be considered as a major breakthrough in performance. Current research includes coupling the presented ion mobility spectrometer to alternative ionization sources to further broaden the measurement possibilities and further resolution enhancement. In addition to that, the option of scaling the presented instrument to the size of a bench top IMS is being evaluated. A dritube based on the current design with a length of 45 cm would theoretically be able to achieve resolutions in excess of 500. The ability to gather structural information with much simpler instrumentation would make IMS a competitor for low-end, small-scale atmospheric pressure chemical ionization mass spectrometers, and allow their users to perform more analytical tasks.

References

1 H. Borsdorf and G. A. Eiceman, Appl. Spectrosc. Rev., 2006, 41, 323–375.
2 G. A. Eiceman and Z. Karpas, Ion Mobility Spectrometry, CRC Press, 2nd edn, 2004.
3 G. A. Eiceman and J. A. Stone, Anal. Chem., 2004, 76(21), 390A–397A.
4 H. | Borsdorf, | T. | Mayer, | M. | Zarejousheghani | and
G. A. Eiceman, Appl. Spectrosc. Rev., 2011, 46, 472–521.
5 A.-E. Kreuder, H. Buchinger, S. Kreuer, Th. Volk, S. Maddula and J. I. Baumbach, Int. J. Ion Mobility Spectrom., 2011, 14(4), 167–175.
6 C. J. Bramwell, M. L. Colgrave, C. S. Creaser and R. Dennis, Analyst, 2002, 127, 1467–1470.
7 S. Armenta and M. Blanco, Analyst, 2012, 137, 5891–5897. 8 Z. Karpas, B. Tilman, R. Gdalevsky and A. Lorber, Anal. Chim. Acta, 2002, 463(2), 155–163.
9 P. Dwivedi, L. M. Matz, D. A. Atkinson and H. H. Hill, Jr, Analyst, 2004, 129, 139–144.

10 G. A. Harris, S. Graf, R. Knochenmuss and F. M. Fern´andez, Analyst, 2012, 137, 3039–3044.
11 N. Budimir, D. J. Weston and C. S. Creaser, Analyst, 2007, 132, 34–40.
12 M. Simpson, D. R. Anderson, C. W. McLeod, M. Cooke and
R. Saatchi, Analyst, 1993, 118, 1293–1298.
13 K. Cottingham, Anal. Chem., 2003, 75(19), 435A–439A.
14 D. C. Swanson, Int. J. Ion Mobility Spectrom., 2011, 14(2–3), 125–136.
15 E. J. Davis, M. D. Williams, W. F. Siems and H. H. Hill, Jr, Anal. Chem., 2011, 83(4), 1260–1267.
16 A. Heptner, P. Cochems, J. Langejuergen, F. Gunzer and
S. Zimmermann, Analyst, 2012, 137, 5105–5112.
17 Ph. Dugourd, R. R. Hudgins, D. E. Clemmer and
M. F. Jarrold, Rev. Sci. Instrum., 1997, 68(2), 1122– 1129.
18 C. A. Srebalus, J. Li, W. S. Marshall and D. E. Clemmer, Anal. Chem., 1999, 71(18), 3918–3927.
19 S. I. Merenbloom, R. S. Glaskin, Z. B. Henson and
D. E. Clemmer, Anal. Chem., 2009, 81(4), 1482–1487.
20 R. S. Glaskin, S. J. Valentine and D. E. Clemmer, Anal. Chem., 2010, 82(19), 8266–8271.
21 W. Netolicky, P. Holmes, F. Fernandez, J. Tice and
B. Musselman, 19th IMSC, Kyoto, 2012.
22 H. Laia, T. R. McJunkin, C. J. Miller, J. R. Scott and
J. R. Almirall, Int. J. Mass Spectrom., 2008, 276(1), 1–8.
23 J. Langejuergen, P. Cochems and S. Zimmermann, Int. J. Ion Mobility Spectrom., 2012, 15(4), 247–255.
24 H. E. Revercomb and E. A. Mason, Anal. Chem., 1975, 47(7), 970–983.
25 A. B. Kanu, M. M. Gribb and H. H. Hill, Jr, Anal. Chem., 2008, 80(17), 6610–6619.
26 A. Kay, Operational Amplier Noise: Techniques and Tips for Analyzing and Reducing Noise, Newnes, 2012.
27 E. Oran Brigham, Fast Fourier Transform and Its Applications, Prentice Hall, 1988.
28 M. Tabrizchi, T. Khayamian and N. Taj, Rev. Sci. Instrum., 2000, 71, 2321–2328.
29 A. V. Tolmachev, B. H. Clowers, M. E. Belov and R. D. Smith, Anal. Chem., 2009, 81(12), 4778–4787.
30 C. A. Hill and C. L. P. Thomas, Analyst, 2003, 128, 55–60.
31 P. | Cochems, | J. | Langejuergen, | A. | Heptner | and
S. Zimmermann, Int. J. Ion Mobility Spectrom., 2012, 15(4), 223–229.
32 A. A. Shvartsburg, Differential Ion Mobility Spectrometry, CRC Press, 2008.
33 E. V. Krylov and E. G. Nazarov, Int. J. Mass Spectrom., 2009, 285(3), 149–156.
34 A. A. Shvartsburg and R. D. Smith, Anal. Chem., 2011, 83(1), 23–29.
This journal is ª The Royal Society of Chemistry 2013 | Analyst, 2013, 138, 5200–5207 | 5207

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

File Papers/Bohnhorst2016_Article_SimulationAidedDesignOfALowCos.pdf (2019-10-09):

ORIGINAL RESEARCH

## Simulation aided design of a low cost ion mobility spectrometer based on printed circuit boards

A. Bohnhorst ¹ & A. T. Kirk¹ & S. Zimmermann¹

Received: 4 May 2016 /Revised: 31 May 2016 /Accepted: 1 June 2016 /Published online: 4 June 2016 # Springer-Verlag Berlin Heidelberg 2016

Abstract Miniaturized low-cost drift tubes with high analytical performance are a key component for the design of powerful and mass-deployable hand-held ion mobility spectrometers. Thus, a simple model that estimates the influence of the geometrical dimensions on the analytical performance is highly desirable for an effective design process. In this work, we present a simple procedure to predict peak distortion based on only the electrical field distribution inside the drift tube, which can be rapidly simulated using the finite element method. A simulation of the ion motion is not required. Based on these results, we developed an ion mobility spectrometer manufactured entirely from standard printed circuit boards (PCB). Since no additional components were used apart from electrical and gas connectors, ion source and metal grids, the presented ion mobility spectrometer is very simple and inexpensive. Nevertheless, the design provides a resolving power of 82 at a drift length of 50 mm and a drift voltage of 3 kV using a tritium ion source and a field switching shutter. The limits of detection for one second of averaging are 80 pptv for acetone, 35 pptv for dimethyl methylphosphonate and 180 pptv for methyl salicylate.

Keywords Drift tube . Simulation . PCB . Printed circuit board . Low cost

Introduction

An ion mobility spectrometer (IMS) is a device for detecting trace gases in air originally developed for detection of explosives and drugs [1]. Within the last decade, IMS entered new markets, for example in medical applications [2, 3] or as detectors for chemicals in industrial environments [4]. To reach an even wider field of possible applications, many research groups are working on new techniques to improve the performance of IMS. However, to push IMS in the mass-deployable hand-held sector, the main focus are basically low prices and a compact and robust design. Therefore, we developed a design which is suitable for low cost and portable applications while maintaining the resolving power of laboratory-grade systems.
The ion separation in a drift tube IMS is the result of ion motion along the axis of the drift tube driven by a homogeneous electrical field. To initiate the measurement, a packet of ions is injected into the drift tube. During their motion, the ions are separated based on their mobility in the present drift gas. At the end of the drift tube, the ions are captured by a detector which converts and amplifies the ion current into a measurable voltage. By plotting the measured voltage over the drift time, i.e. the time the ions need to reach the detector, a spectrum is obtained. Without interferences, each ion species will create a Gaussian shaped peak in the spectrum, which can be used to identify the components of the ionized gas.
Two important parameters which characterize the performance of an IMS are the resolving power (Rp) and the limits of detection (LOD). The resolving power is defined as the quotient of the drift time td and the full width at half maximum (wFWHM) of the corresponding Gaussian peak in the spectrum.

Rp ¼ td

wFWHM

ð1Þ

* A. Bohnhorst
bohnhorst@geml.uni-hannover.de
1 | Institute of Electrical Engineering and Measurement Technology,
| Leibniz University Hannover, Appelstr. 9A, 30167 Hannover, Germany

Int. J. Ion Mobil. Spec. (2016) 19:167–174 DOI 10.1007/s12127-016-0202-7


Therefore, it is a measure for the ability to separate substances with similar mobilities. A low resolving power might lead to a spectrum with overlapping peaks, while a high resolving power yields a clear separation of all visible components. The limit of detection refers to the systems capability to detect a given substance. Typically, the LOD is defined as the concentration generating a signal amplitude equal to three times the standard deviation of the noise. Thus, a large signal-to-noise-ratio (SNR) is essential for achieving good limits of detection.

Simulation based design process

A typical drift tube IMS basically consists of three parts - the ion source, the drift tube and the detector. Of these components, the drift tube typically is the largest, includes the highest number of components and therefore most likely provides the highest optimization potential.
The required space for the drift tube is determined by its length Ld and its outer radius rout. Since the systems resolving power is determined by the length Ld and the peak width due to injection winj and amplifier wamp as shown in Eq. (2), we cannot reduce the length without improving the ion shutter and amplifier if a constant resolving power is required [5].

Rpe³

# ffiffiffiffiffiffiffiffiffiffiffiffiffiffiffiffiffiffiffiffiffiffiffiffiffiffiffiffi

L²

# d ffiffiffiffiffiffiffiffiffiffiffiffiffiffiffiffiffiffiffiffiffiffiffi

w²
in j þ w²

amp q

vuut | ð2Þ

However, there is no immediate impact of the outer radius rout on the resolving power. Nevertheless, a homogenous electrical field is imperative for maintaining IMS resolving power, thus creating an indirect influence of the outer radius on the resolving power. Therefore, it is necessary to analyze the relationships between rout and the electrical field distribution E(x, r), which is illustrated inside the drift tube in Fig. 1. While the field is homogeneous on the axis of symmetry marked by the dashed line, distortions arise near the electrodes due to the constant electrical potential on a drift ring. As the ion trajectories will follow the streamlines of the electrical field due to the constant collisions with the drift gas, ions far from the axis of symmetry will take a longer, curved path (blue line) compared to the trajectories close to the axis (red line). Thus, the drift time of an ion depends not only on its mobility, but also on its radial position inside the drift tube, which can lead to ions with the same mobility arriving at different drift times [6]. As this phenomenon only causes delay, it leads to peak tailing

Fig. 1 Distribution of the electrical field E(x,r) in a simplified geometrical model. The length of the drift tube Ld is determined by the number of rings nring and the pitch pring between two guard ring centers. The outer radius of the tube rout is given by the ring depth dring and the inner radius rin


Fig. 2 On the left half, a simulation of the signal (dashed) resulting from distorted and delayed ion plugs (solid lines) reaching the detector is shown. On the right half, an enlargement of the peaks corresponding to the five most distorted ion plugs is shown. The data are generated by solving the ion motion in the field distribution presented in Fig. 1

168 | Int. J. Ion Mobil. Spec. (2016) 19:167–174


and may reduce the analytical power of the drift tube due to broader and therefore lower peaks. A common method to ensure a clear Gaussian peak shape in the presence of field distortions is masking ions traveling far from the axis of symmetry. Unfortunately, this will lead to a lower signal amplitude and therefore a lower SNR.

Numerical field simulations

To generalize the simulations, the radius r measured from the axis of symmetry as shown in Fig. 1 will be described in terms of the normalized radius Γ, where Γ is given by the radius r divided by the inner tube radius rin.

### Γ ¼ r

rin

ð3Þ

To begin with, it is necessary to determine the relationship between ring dimensions and peak shape. To do so, the ion distribution on the detector plane was calculated by simulating the ion trajectories in a given field distribution employing COMSOL Multiphysics using the Transport of Diluted Species module. The generated data can be used to evaluate the time related ion flux at each point of the detector in terms of the normalized radius Γ.
Simulating the ion trajectories in an electrical field as the one shown in Fig. 1 a peak shape as illustrated by the dashed line on the left half of Fig. 2 can be obtained. Dividing this integrated signal into a number of discrete ion plugs (solid lines) moving on different normalized radiuses Γ allows a detailed analysis of the relationship between the distribution of the electrically field and the overall peak shape.

Fig. 3 In the first panel, the ion distribution calculated by using only the axial distribution of the electrical field is shown. In the middle, the correction for the radial ion motion is included. The last panel shows the accurately computed ion distribution for comparison


Fig. 4 Normalized resolving power (dotted), ideality factor (solid) and electrical field approximation (dashed) as a function of the normalized radius Γ


Fig. 5 Effectively usable radius Γeff as a function of wring/pring for dring/ pring =2(circle), dring/pring =1 (cross) and dring/pring = 0.5 (triangle). The inner tube radius is equal to the pitch (rin/pring = 1)

Int. J. Ion Mobil. Spec. (2016) 19:167–174 | 169


As illustrated in the right half of Fig. 2, ion plugs closer to the axis of symmetry (1.) are nearly Gaussian shaped, while plugs moving close to the electrodes are delayed and asymmetrically broadened (5.). As most ion plugs move in a homogenous field, the integrated signal shown in the left half of Fig. 2 is similar to a Gaussian peak with the expected drift time (dotted line), but reveals a small tailing. Thus, we define an effective radius Γeff including all trajectories without significant negative impact on the peak shape. Γeff therefore describes the effective usable radius of the drift tube.
To decide which of the illustrated ion plugs can be included without deforming the integrated peak, a mathematical measure for peak deformation is required. The resolving power Rp might be the obvious candidate, as it is the most common criterion for the analytical performance of IMS and is also easy to measure. However, as it is based on the full width at half maximum, it will be insensitive to tailing which occurs far below the half height of the peak, such as the distortion shown on the left hand side of Fig. 2. To circumvent this problem, we propose the ideality factor η as the peak height hpeak divided by the peak area Apeak as given by Eq. (4).

η ¼ hpeak

Apeak

ð4Þ

As every kind of peak broadening, no matter its shape, must lead to a reduction of peak height at a given peak area, the ideality factor η can be expected to react much more sensitively to the peak tailing shown in Fig. 2. Normalization yields an ideality factor which is 1 for the Gaussian shaped peaks moving on the axis of symmetry and < 1 for deformed peaks. For example, on the right hand side of Fig. 2, the normalized values of η would be 0.97 for peak 1 and 0.18 for peak 5. The respective normalized resolving power would

Fig. 6 Simulation of the electrical field corresponding to dring/pring equal 2, 1, 0.5 and 0.13 (left to right) in presence of a grounded electrode surrounding the drift tube


Fig. 7 Effectively usable tube radius Γeff (circles) as a function

of wring/pring (rin/wring = 7.5, dring/
wring = 0.1) and fit with a x⁽³/2) function (line). The second x-axis shows the number of rings nring required in an IMS with a drift length of 100 mm


be 0.95 and 0.20. However, when analyzing the resulting peak shown on the left hand side of Fig. 2, the normalized ideality factor is 0.71, while the normalized resolving power remains at 0.95. Thus, only the ideality provides a useful mathematical measure for peak deformation in this case.
Unfortunately, calculating either η or Rp requires numerical simulations of ion trajectories, which are much more time consuming than the calculation of the electrical field, as they must be solved for every time step of the simulation instead of only once. Thus, a parameter sweep sufficiently resolved for drift tube development would consume too much time to be feasible. Therefore, we propose a third method, which provides an approximation based on only the electrical field distribution E(x,r), which can be simulated within seconds or minutes. It is based on a two-step approach:
First, the peak position is calculated as a function of Γ. To do so, the inverse of the axial component of the electrical field multiplied by the inverse mobility K is integrated along the length of the drift tube at the given Γ, which serves as a measure for the drift time along this line.

ΔtdðÞ Γ ¼

# Z Ld

0

1
EðÞ x;Γ ⋅K
dx | ð5Þ

This value is then normalized to the result at Γ= 0, which is just the length of the drift tube Ld squared divided by the drift voltage Ud due to the homogenous field at this position.

td ¼ Ld

2
Ud⋅K | ð6Þ

The result is a measure for the delay of the peak at the given Γ compared to its ideal drift time td.

ΔtdðÞ Γ

td

¼
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

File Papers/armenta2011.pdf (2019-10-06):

Analytica Chimica Acta 703 (2011) 114–123

Contents lists available at ScienceDirect (http://www.sciencedirect.com/science/journal/00032670)

# Analytica Chimica Acta

journal homepage: www.elsevier.com/locate/aca

### Review

## A review of recent, unconventional applications of ion mobility spectrometry (IMS)

## Sergio Armenta∗, Manel Alcala, Marcelo Blanco

Department of Chemistry, Faculty of Sciences, Universitat Autònoma de Barcelona, E-08193 Bellaterra, Barcelona, Spain

a r t i c l e i n f o

Article history:
Received 6 June 2011
Received in revised form 12 July 2011 Accepted 14 July 2011
Available online 23 July 2011

Keywords:
Ion mobility spectrometry
Pharmaceuticals
Food analysis
Environmental analysis
Clinical analysis
Process control

a b s t r a c t

The applications of ion mobility spectrometry (IMS) have grown exponentially beyond its uses for explosive, illicit drug and chemical warfare agent monitoring in recent years. Instrumental developments includingnew drifttubematerials andionizationsourceshave enabledthemanufacturing ofmore sophisticated and affordable IMS equipment for the advantageous analysis of samples with no pretreatment. The most recent applications of IMS include quality control and cleaning validation procedures in the pharmaceutical industry; determinations of contaminants in food samples; clinical analyses of biological fluids; environmental analyses of contaminants in gaseous, liquid and solid samples; and (bio)process quality control monitoring. Coupling IMS with MSn has enabled the analysis of very complex samples and the extraction of knowledge unavailable from isolated MS measurements, especially in the polymer and petroleomic industries.
© 2011 Elsevier B.V. All rights reserved.

Dr. Armenta obtained his PhD in analytical chemistry at the Universitat de València in 2006. He is currently a senior researcher of analytical chemistry at the Applied Chemometrics Research group at the Universitat Autònoma de Barcelona. His research topics included coupling of automated flow systems with IR and Raman spectroscopic detection and vibrational spectroscopy combined with chemometrics. His current research fields include the development of fast and sensitive analytical methodologies based on ion mobility spectrometry.

Dr. Alcala is Lecturer Professor of the Applied Chemometrics Research group at the Universitat Autònoma de Barcelona. His main research topics are quality assurance and quality control, process analyticaltechnology and quality by design in the pharmaceutical industry, using molecular spectroscopy techniques combined with multivariate data analysis methods.
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

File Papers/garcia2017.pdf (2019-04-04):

ORIGINAL RESEARCH

## An open source ion gate pulser for ion mobility spectrometry

Luke Garcia¹ & Carolyn Saba¹ & Gabriela Manocchio¹ & Gordon A. Anderson² &
Eric Davis¹ & Brian H. Clowers ³

Received: 2 October 2017 /Accepted: 5 October 2017
# Springer-Verlag GmbH Germany 2017
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

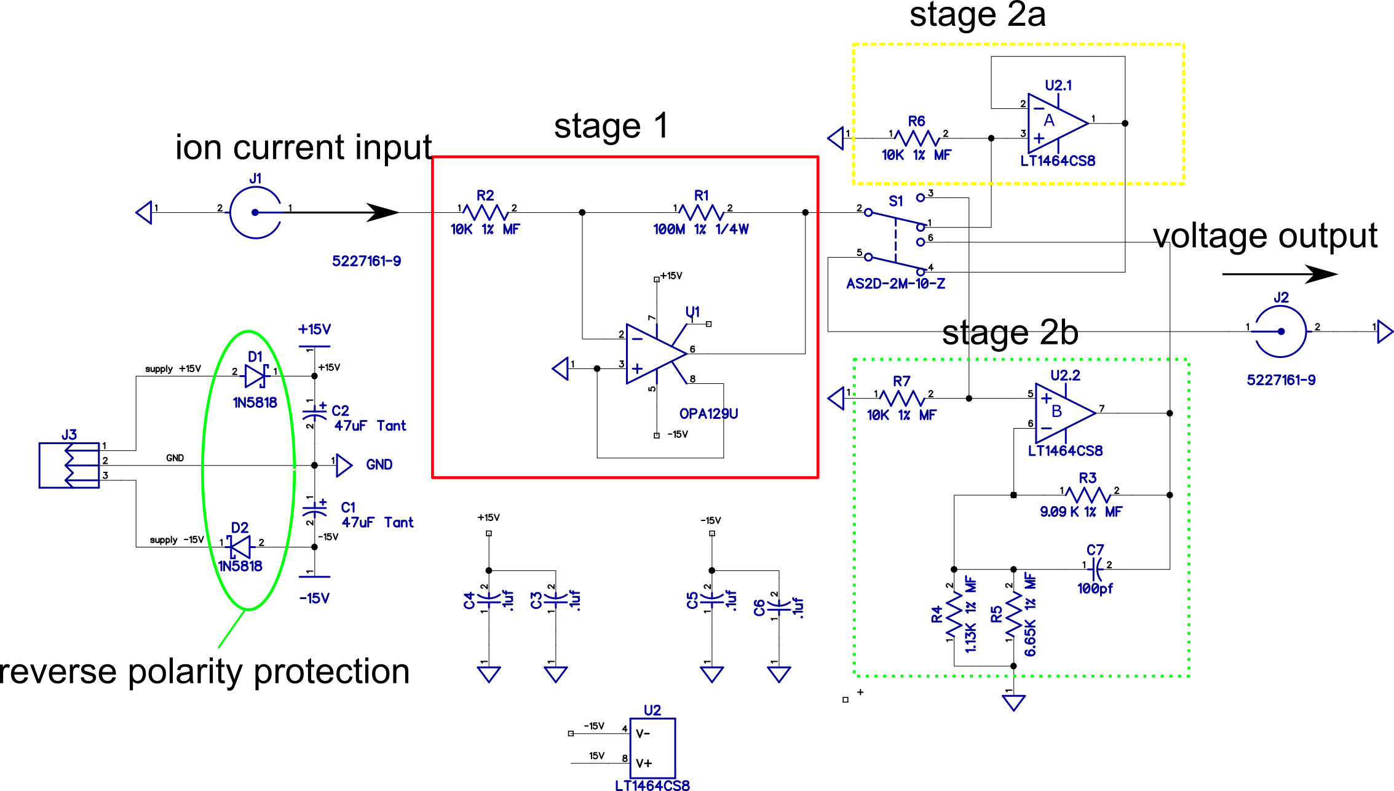
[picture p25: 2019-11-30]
OS-IMS-master/PCB_IMS/Figures/schematic amp.png

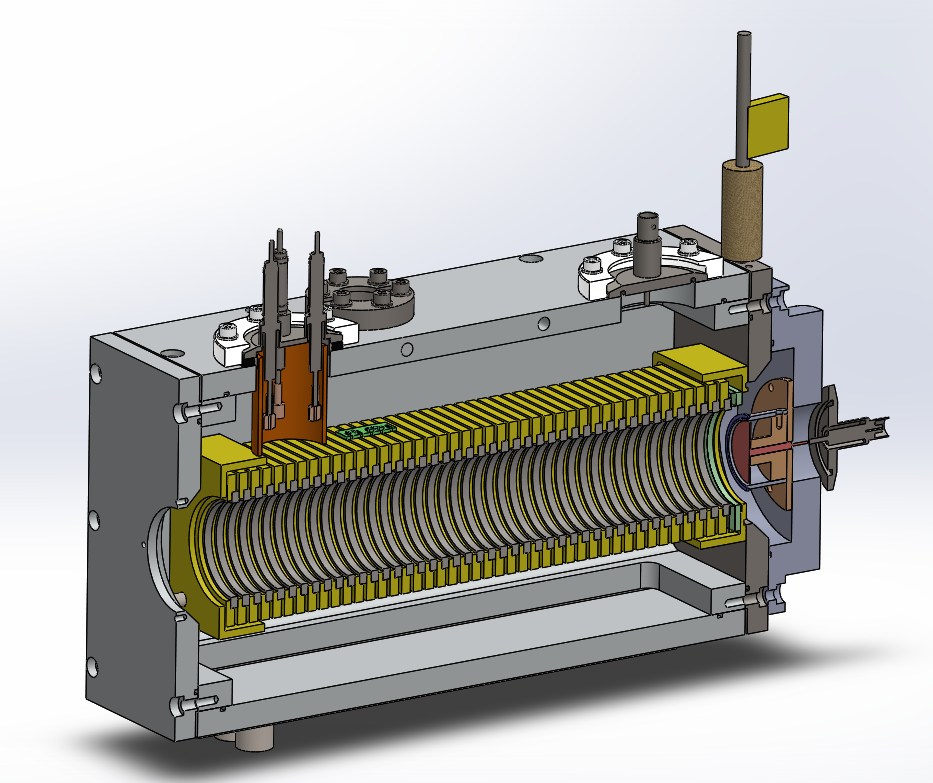
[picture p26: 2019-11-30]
OS-IMS-master/APIMS_Schematic.PNG

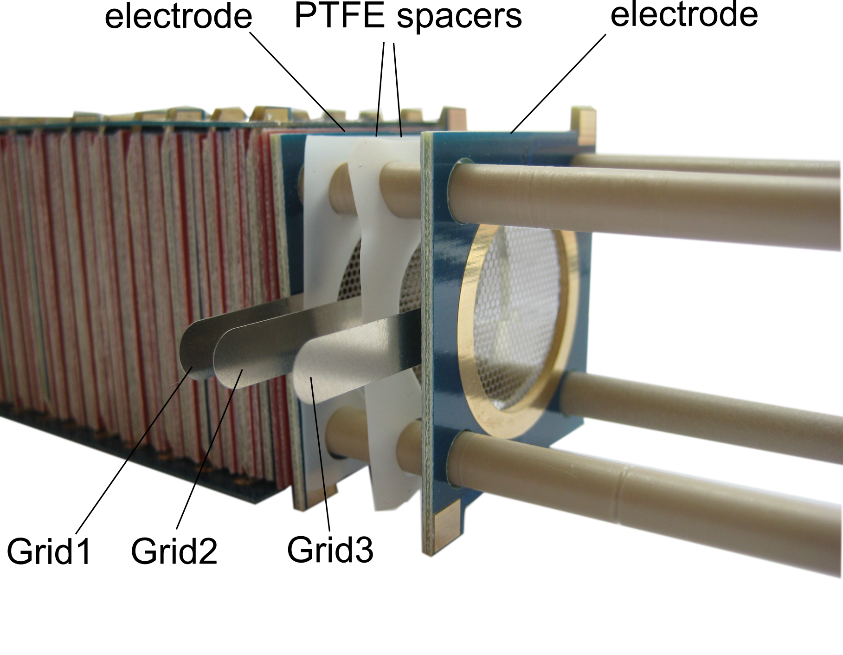
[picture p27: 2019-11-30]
OS-IMS-master/PCB_IMS/Figures/Foto shutter.png

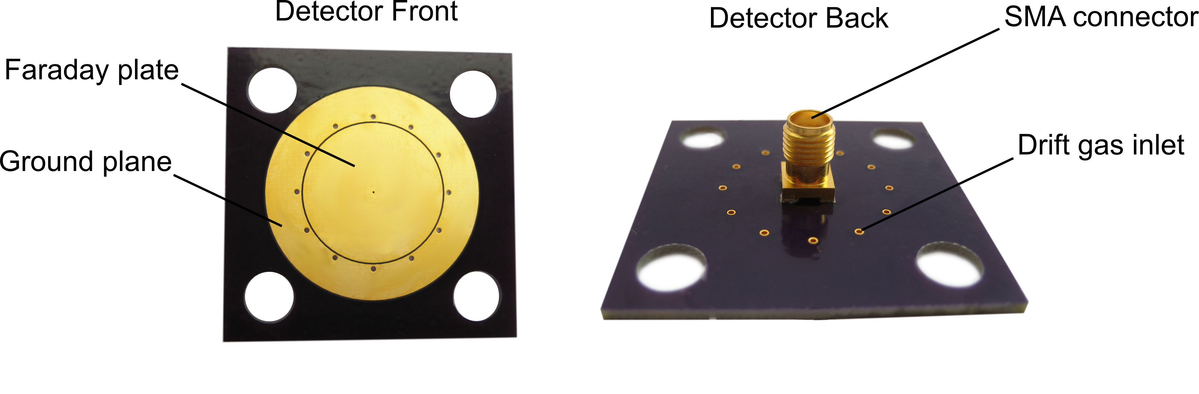
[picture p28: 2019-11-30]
OS-IMS-master/PCB_IMS/Figures/text958-5-3.png

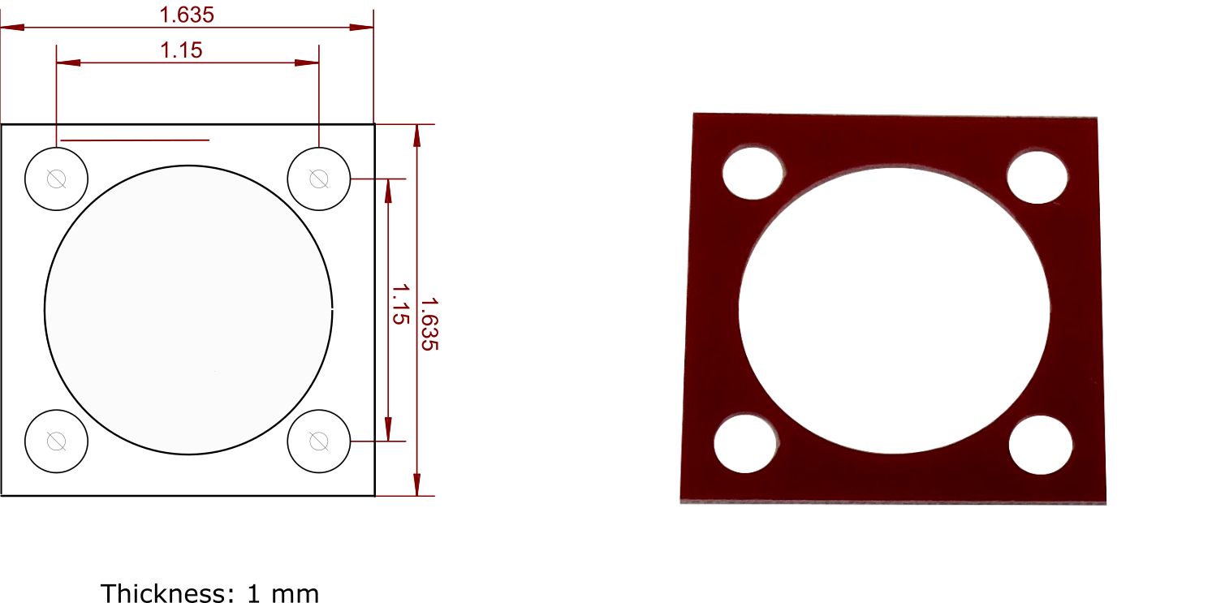
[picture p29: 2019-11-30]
OS-IMS-master/PCB_IMS/Figures/spacer.png

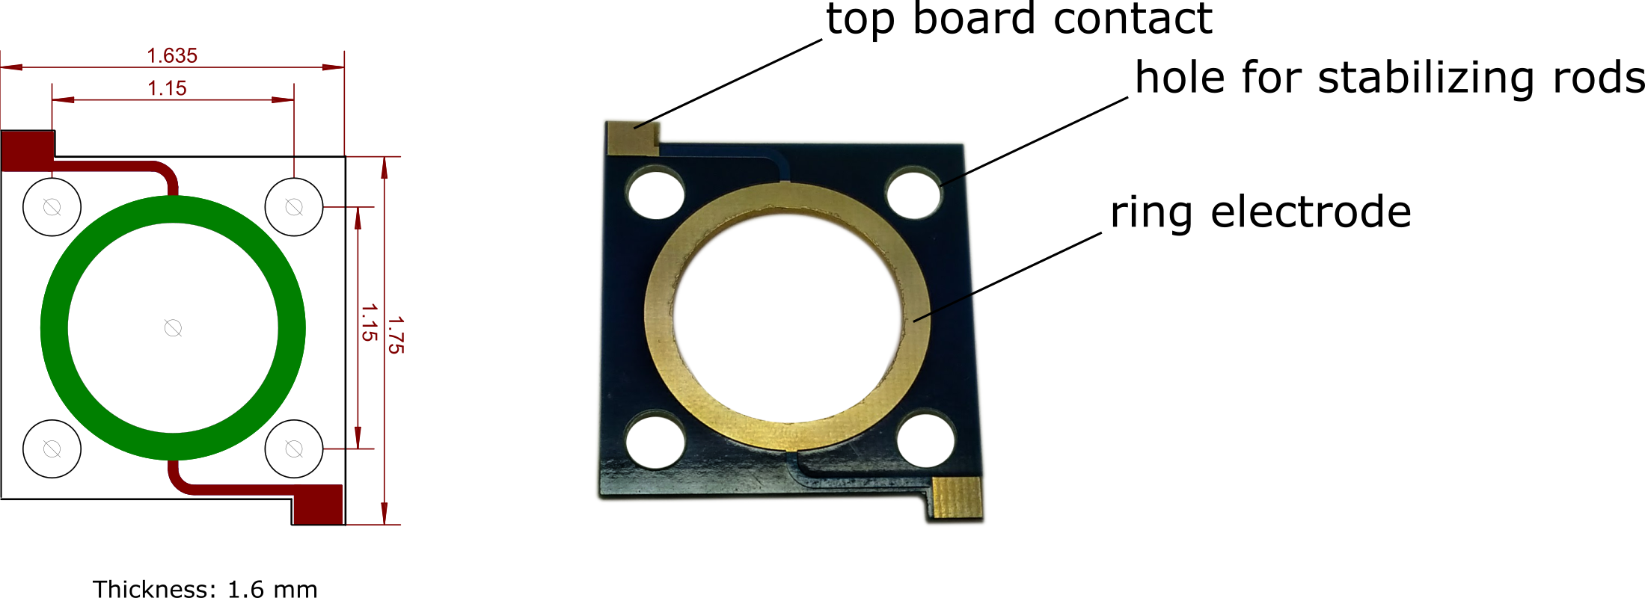
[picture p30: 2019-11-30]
OS-IMS-master/PCB_IMS/Figures/electrode.png

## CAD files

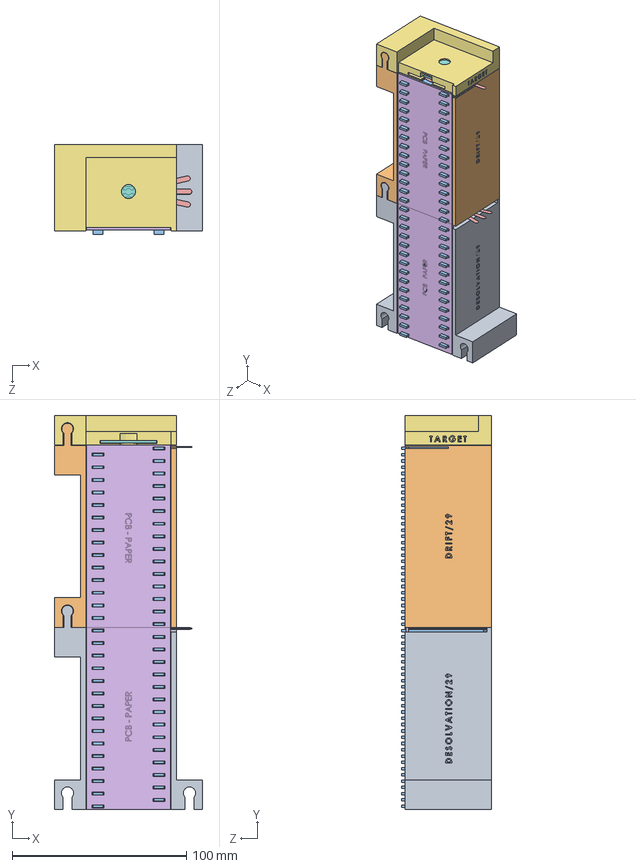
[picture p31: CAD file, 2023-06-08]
CAD/V3/Assembly_grid_shutter.SLDASM
85.0 x 226.1 x 51.6 mm
Diffusion_region_29_electrodes_grid_shutter
Drift_region_29_electrodes_grid_shutter
Electrode x 58
Grid_spacer x 2
grid x 4
PCB_paper x 2
Cible_region_gas
Cible

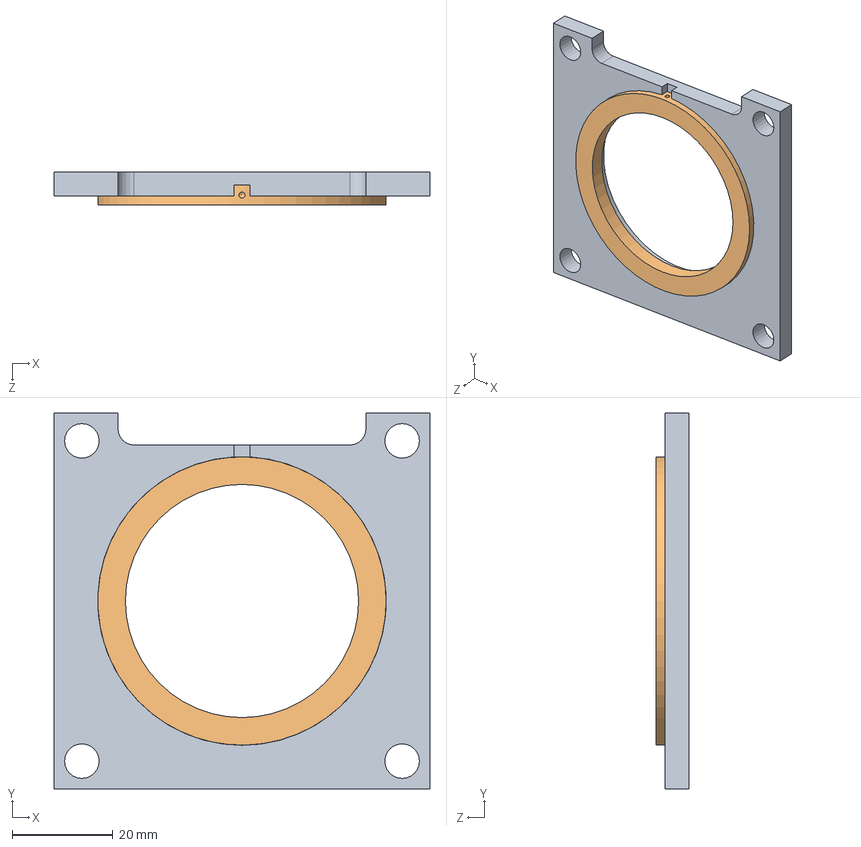
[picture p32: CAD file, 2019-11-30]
OS-IMS-master/AP_IMS_Assembly_6inch_23Sept2016/RingMonomer_v3.SLDASM
74.5 x 74.5 x 6.53 mm
Insulating_Ring_v1
Core_Ring_Flat

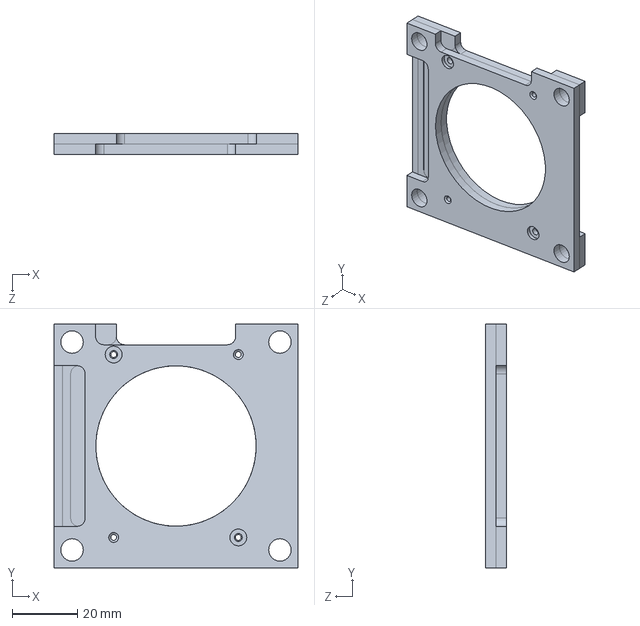
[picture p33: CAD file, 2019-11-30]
OS-IMS-master/AP_IMS_Assembly_6inch_23Sept2016/Gate_Assembly_v2.SLDASM
74.5 x 74.5 x 6.32 mm
Gate_Ring_v2 x 2

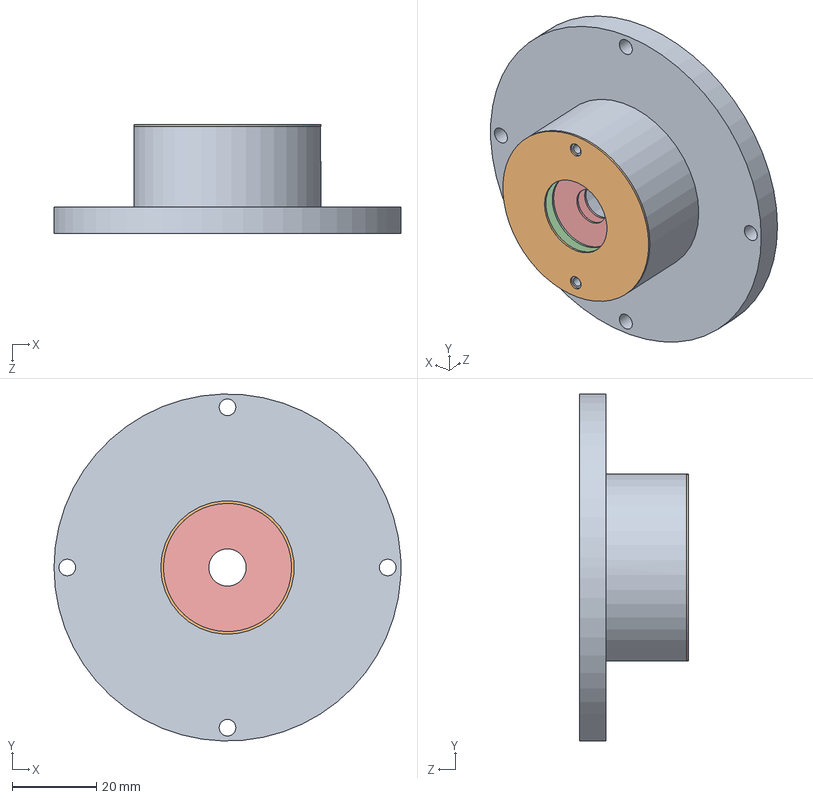
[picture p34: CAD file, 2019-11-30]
OS-IMS-master/AP_IMS_Assembly_6inch_23Sept2016/ESI_Ring_Assembly.SLDASM
82.5 x 82.5 x 25.9 mm
ESI_Ring_Housing
ESI_Terminal_Ring
ESI_Insulating_Ring x 3
ESI_Ring_LargeID
ESI_Ring_SmallID x 2

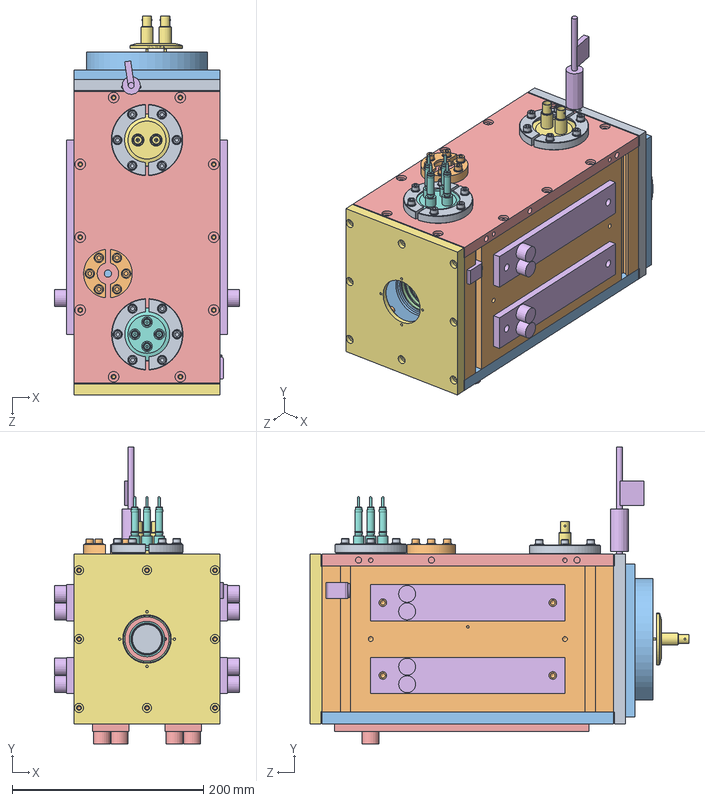
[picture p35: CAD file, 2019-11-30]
OS-IMS-master/AP_IMS_Assembly_6inch_23Sept2016/AP_IMS_Assembly_6inch.sldasm
193.7 x 310.2 x 396.4 mm
AP_Housing_Back_NSF_Thin
IMS_Ceramic_Rod x 4
Faraday_Chamber_2014
Faraday_Grid_Holder
Faraday_Insulator_A
Faraday_Insulator_B
BNC_2x_KF40 x 2
Faraday_Grid_Ring
Faraday_Plate
AP_Housing_6inch
PEEK_Cover
Shield_Cap
Housing_Lid_6inch
ISO_63_SCP
AP_Housing_Front_6inch
KF40_20kv_4Pin_SST_FA13219
KF40_Bulkhead x 2
Push_On_Connector x 4
Housing_Bottom_6inch
Voltage_Divider_Monomer
StripHeater_12 x 2
StripHeater_10 x 4
P101962
HV_Feedthrough_Shield
PEEK_Cover_Rear_V2
KF16_Bulkhead
Insulating_Ring_v1 x 43
Core_Ring_Flat x 43
Gate_Ring_v2 x 2
Gas_Heater_mockup

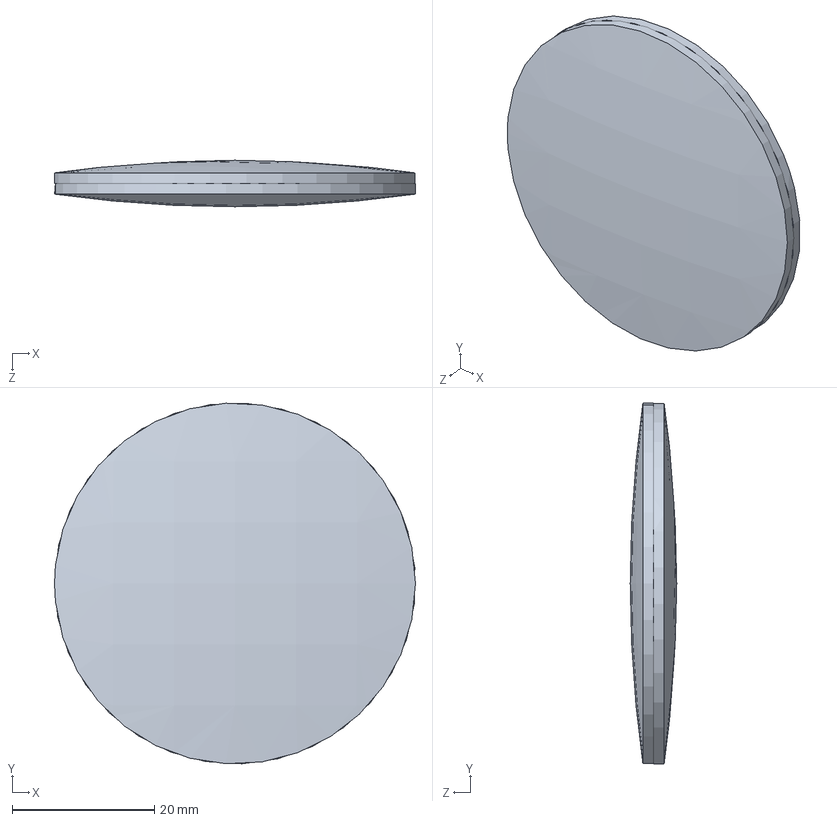
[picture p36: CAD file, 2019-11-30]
OS-IMS-master/AP_IMS_Assembly_6inch_23Sept2016/200 mm lens.SLDASM
50.8 x 50.7 x 6.55 mm
200 mm lens half x 2

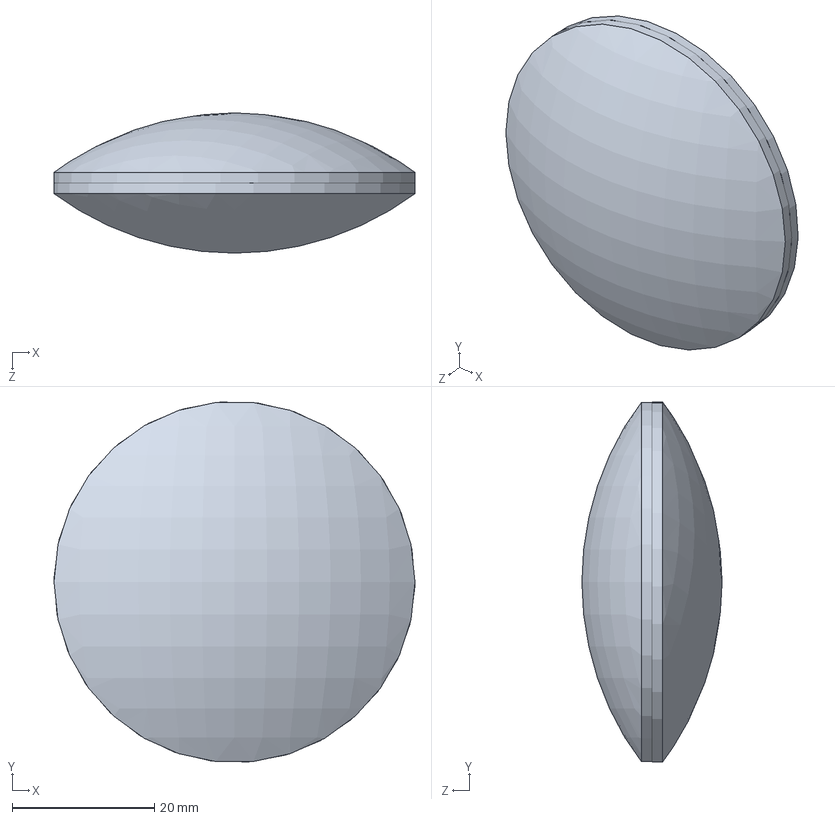
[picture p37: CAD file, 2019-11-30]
OS-IMS-master/AP_IMS_Assembly_6inch_23Sept2016/50.2 mm lense.SLDASM
50.8 x 50.6 x 19.7 mm
50.2 mm lens half x 2

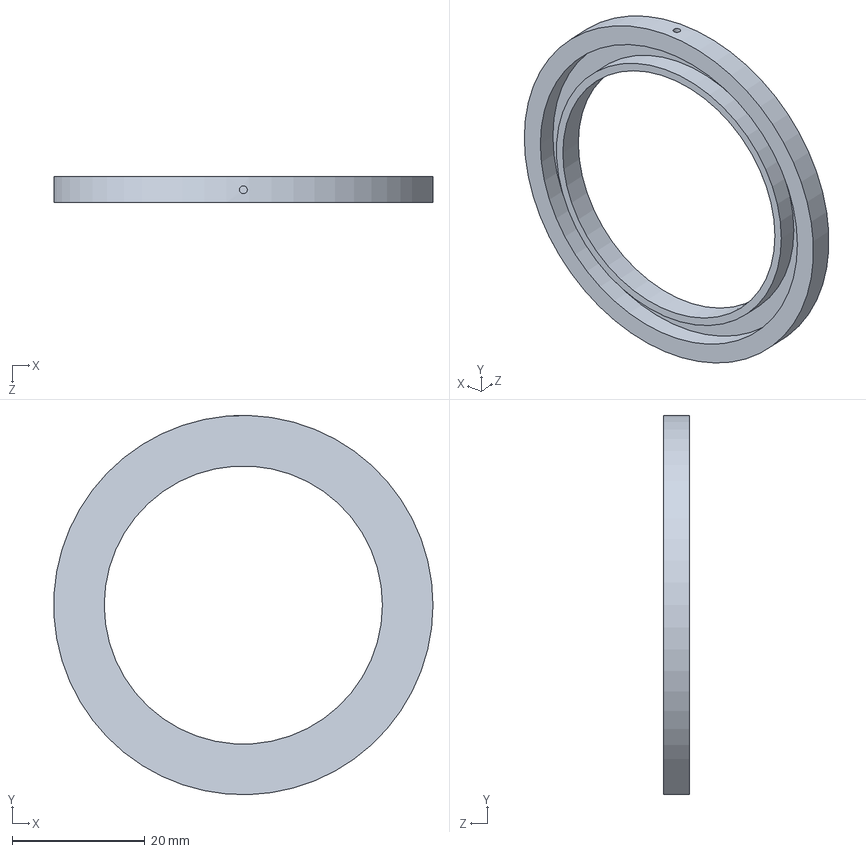
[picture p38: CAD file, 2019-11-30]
OS-IMS-master/AP_IMS_Assembly_6inch_23Sept2016/GAS_RING_MONOMER.SLDASM
57.1 x 57.1 x 3.92 mm

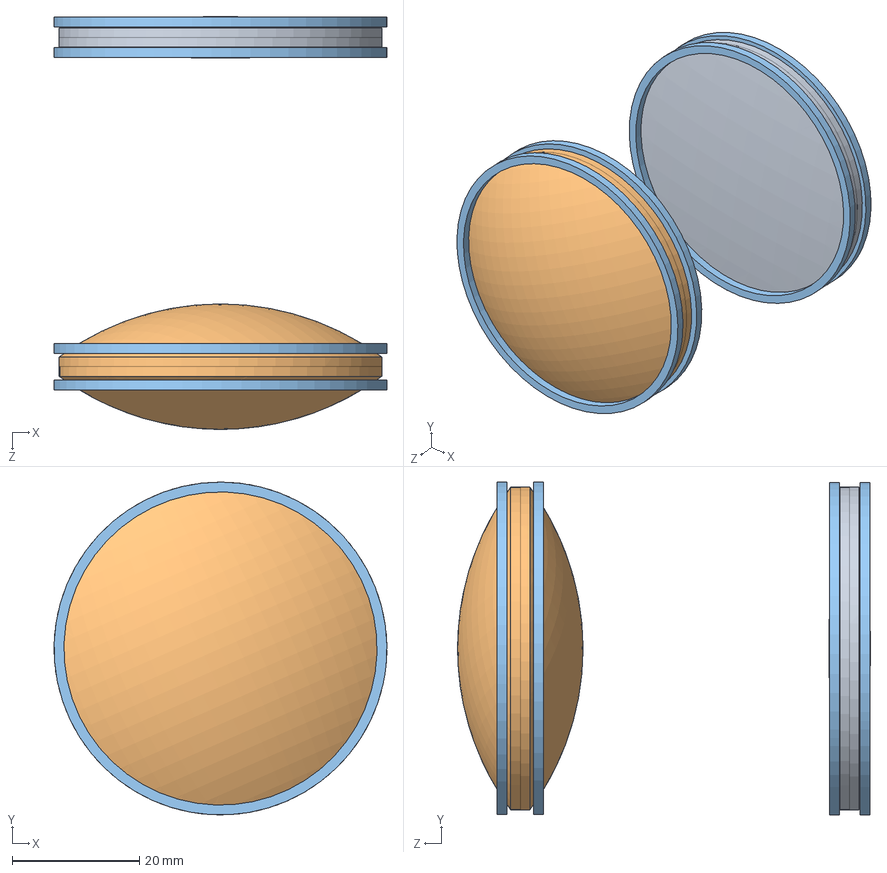
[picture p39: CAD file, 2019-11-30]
OS-IMS-master/AP_IMS_Assembly_6inch_23Sept2016/Lens Mount with lenses.SLDASM
52.3 x 52.3 x 64.9 mm
200 mm lens half x 2
50.2 mm lens half x 2
Lens Ring x 4

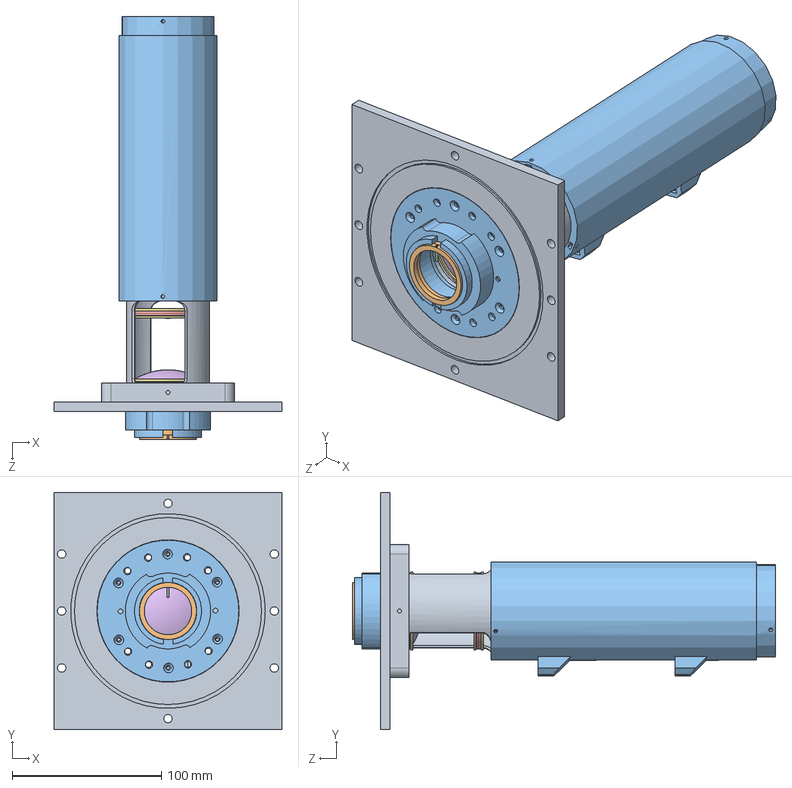
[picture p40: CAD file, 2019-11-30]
OS-IMS-master/AP_IMS_Assembly_6inch_23Sept2016/RIIN_Assembly_Davis - Mounted Lenses.SLDASM
152.4 x 158.8 x 283.0 mm
RIIN Chamber Housing
RIIN Ap Grid Holder 1
RIIN Ap Grid Holder Spacer One PieceTeflon
RIIN ESI Guide
200 mm lens half x 2
50.2 mm lens half x 2
Lens Ring x 4
SM2L30C-Solidworks
ESI_Grid_Spacer
Lens Tube Extension - 7.5in

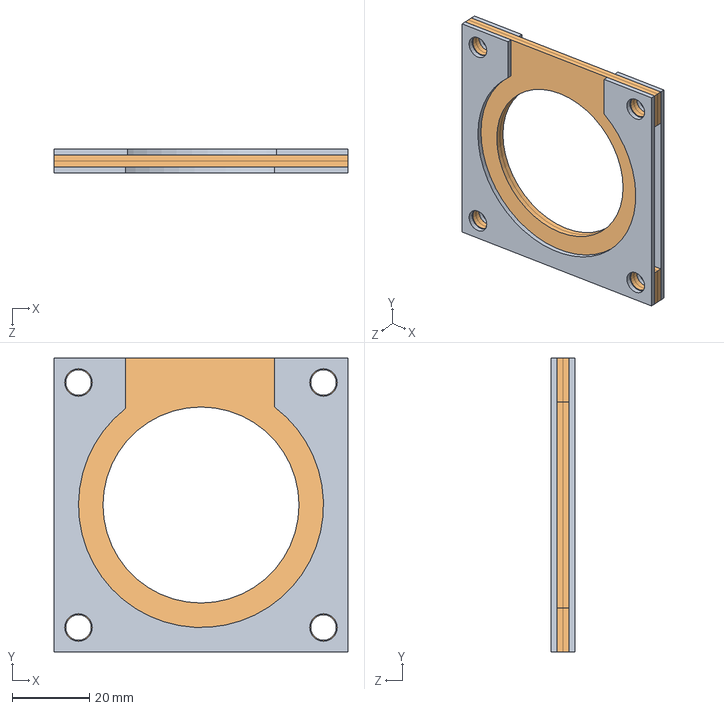
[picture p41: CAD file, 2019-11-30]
OS-IMS-master/AP_IMS_Assembly_6inch_23Sept2016/Gate_Assembly.SLDASM
76.2 x 76.2 x 6.35 mm
Gate_Spacer_3_inch x 2
Gate_Ring_2_inch x 2

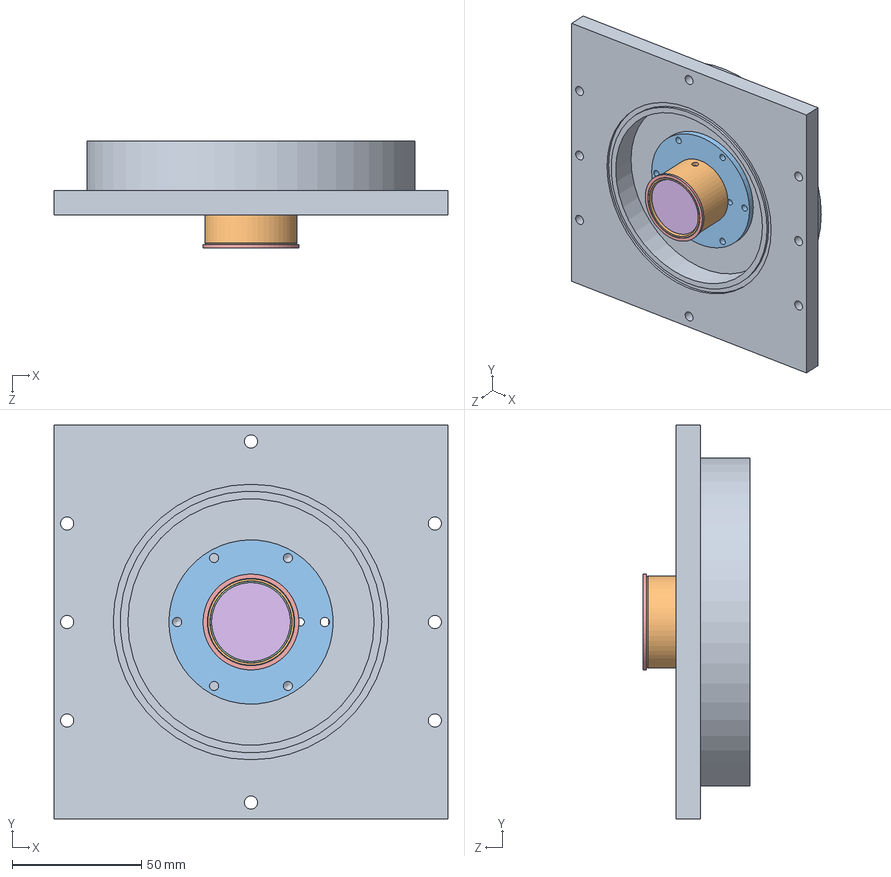
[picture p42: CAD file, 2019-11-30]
OS-IMS-master/AP_IMS_Assembly_6inch_23Sept2016/Faraday_Assembly.SLDASM
152.4 x 152.4 x 41.3 mm
Faraday_Chamber_2014
Faraday_Grid_Holder
Faraday_Insulator_A
Faraday_Insulator_B
Faraday_Grid_Ring
Faraday_Plate

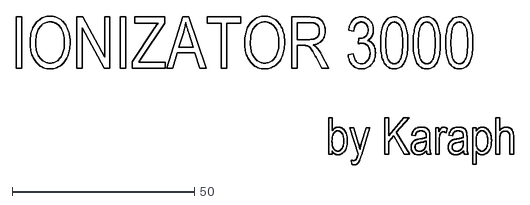
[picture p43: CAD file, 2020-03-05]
CAD/catia V1/DRAWING1.dxf
136.3 x 40.8

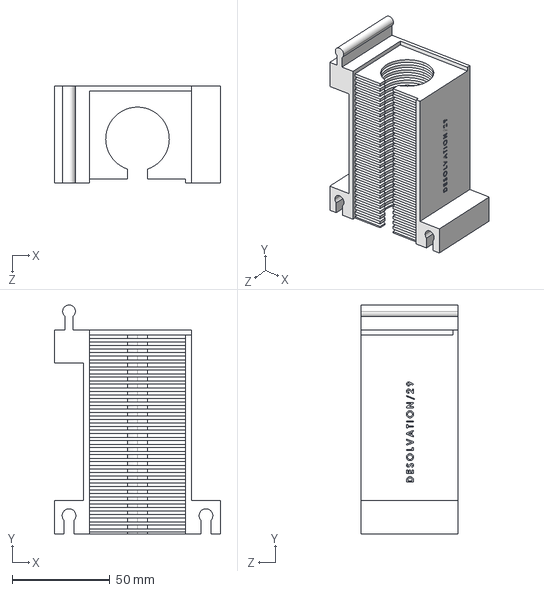
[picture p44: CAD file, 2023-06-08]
CAD/V3/Diffusion_region_29_electrodes_grid_shutter.STEP
85.0 x 117.1 x 49.5 mm

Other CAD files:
OS-IMS-master/AP_IMS_Assembly_6inch_23Sept2016/KF25_Bulkhead.SLDPRT
OS-IMS-master/PCB_IMS/1_Spacers/1b_Spacer.STL
OS-IMS-master/PCB_IMS/2_Electrodes/2b_Electrode.STL
OS-IMS-master/PCB_IMS/Grid_WSU_v2.SLDPRT
CAD/V2/CAD simulated PCBs/Cible.3MF
CAD/V2/CAD simulated PCBs/Cible.STEP
CAD/V2/CAD simulated PCBs/Electrode.3MF
CAD/V2/CAD simulated PCBs/Electrode.SLDPRT
CAD/V2/CAD simulated PCBs/Electrode.STEP
CAD/V2/CAD simulated PCBs/PCB_desolvation_region_KR.3MF
CAD/V2/CAD simulated PCBs/PCB_desolvation_region_KR.SLDPRT
CAD/V2/CAD simulated PCBs/PCB_desolvation_region_KR.STEP
CAD/V2/CAD simulated PCBs/PCB_drift_region_KR.3MF
CAD/V2/CAD simulated PCBs/PCB_drift_region_KR.SLDPRT
CAD/V2/CAD simulated PCBs/PCB_drift_region_KR.STEP
CAD/V2/Cible region (target)/Cible_region.3MF
CAD/V2/Cible region (target)/Cible_region.SLDPRT
CAD/V2/Cible region (target)/Cible_region.STEP
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

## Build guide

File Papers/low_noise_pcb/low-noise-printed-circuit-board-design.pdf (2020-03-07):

# Low Noise Printed Circuit Board Design

## Matt Affeldt

November 16, 2012

Design Team 6 – ECE480

## Keywords:

Low Noise, Impedance, Capacitance, PCB,

Printed Circuit Board, layout, design

## Summary:

This application note is intended to be a guide for low noise, high efficiency designs of printed circuit boards (PCB). This includes mainly layout considerations of PCBs to limit EMI between components as well as dealing with some non-board generated noise issues.

Low Noise PCB Design

ECE480 Fall 2012 2 of 9

## Table of Contents

Low Noise PCB Design

ECE480 Fall 2012 3 of 9

## Introduction

In this application note, how to design a printed circuit board (PCB) to be low noise in order to improve the quality of the desired circuit will be described. It is assumed that the reader has some background knowledge of the circuits, but the basics of printed circuit boards will be described. Designing low noise printed circuit boards requires avoiding excess impedance, stray capacitance, and antennas. Any large impedances, stray capacitance or antennas can cause noise, instability or both. Noise is typically a high-frequency signal on top of the desired signal. This noise can often interfere with measurement techniques and can introduce a significant amount of inaccuracy in the results depending on how noisy the circuit is. Instability, on the other hand, is much worse. Instability can cause complete failure of a circuit and potentially damage components in the circuit. Stability concerns are commonly found with operational amplifiers, and are also a concern when using most active components such as microcontrollers and power converters. Poor planning can lead to oscillating signals which can eventually grow, swinging voltage from ground to the power supply voltage and creates large current. This application note will detail how to reduce noise, improve performance and avoid circuit instability.

## Printed Circuit Board Background

A printed circuit board is a layer of copper that has been cut or etched in order to create electrical connections between pads. These pads will then be connected to a component in order to realize a specific circuit in a cleaner, more compact form than a bread board (or proto-board). These copper layers can be stacked with an insulating epoxy in between to allow very complex circuits to be realized on a dimensionally small board. Each layer will only make the board slightly thicker but not any wider or longer. Each connection from one pad to another is called a trace. When it is necessary to connect one trace to another trace on a different layer, a via can be used which is a hole that is plated with conductive material. Finally, in multi-layer boards it is common to have ‘power planes’ such as ground and the power supply voltage to make it easy to power and ground all the components. There is no perfect way to design a printed circuit board. There are some specific do’s and don’ts but generally speaking, design choices involve tradeoffs in performance between two or more attributes.

Low Noise PCB Design

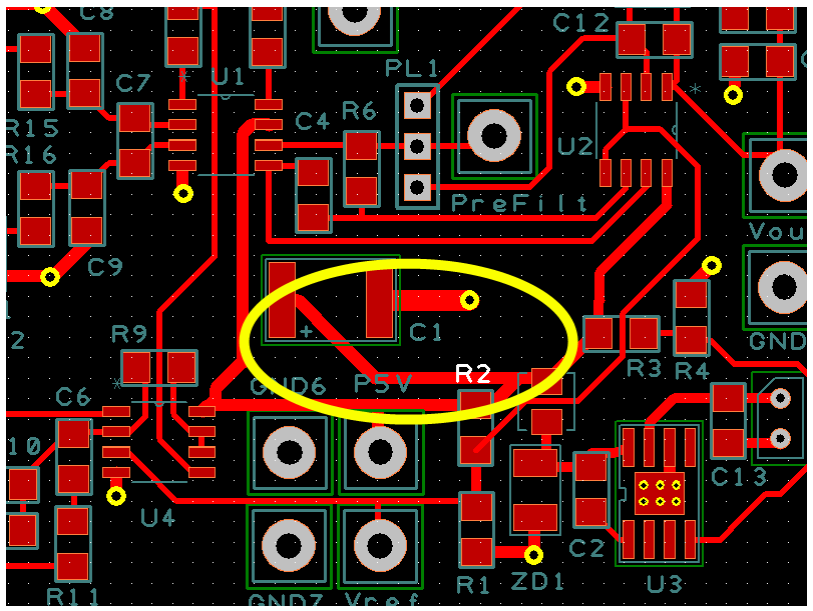
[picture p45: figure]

ECE480 Fall 2012 4 of 9

## Printed Circuit Board Design

This section will describe how to design PCBs to reduce internal noise generated by the circuit components and physical layout of the board. This includes suggestions to reduce impedance across traces as well as how to keep the paths across the ground plane very low impedance, avoid stray capacitance, avoid unwanted inductance, and avoid creating antennas. This section also discusses some brief stability issues and how to design a PCB to avoid situations that can result in circuit instability.

### Reducing Impedance

High impedance is the easiest noise source to mitigate, below are 2 examples of how to reduce impedance-based noise from the circuit.

1. Avoid long traces. Long traces are inherently more resistive than short traces. Below in Figure 1 shows a bad example of how to lay out a component. There is a long trace between power and the capacitor (which is polarized). Figure 2 shows that it is possible, by rotating the capacitor 180° and moving it to the right, to make the trace much shorter so as to result in a lower impedance for the trace.

Figure 1. Long trace for connecting capacitor to power

Low Noise PCB Design

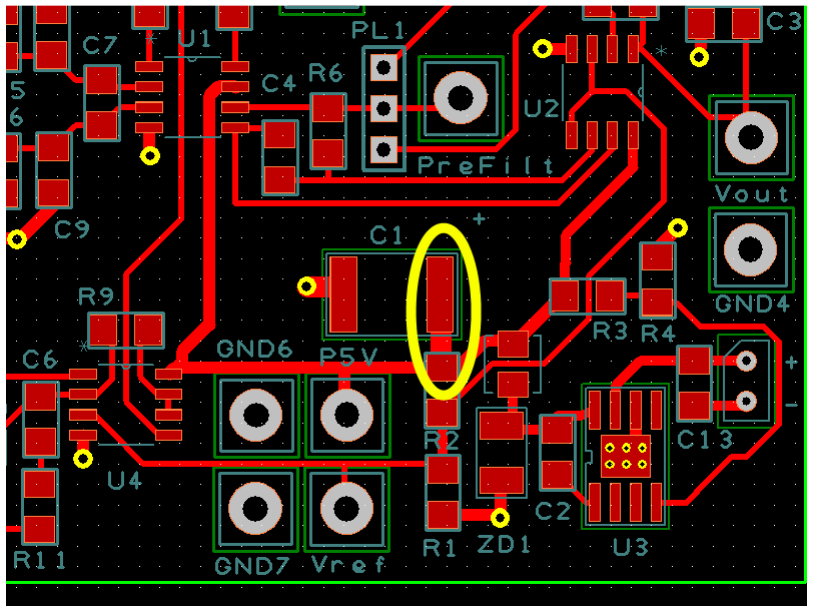
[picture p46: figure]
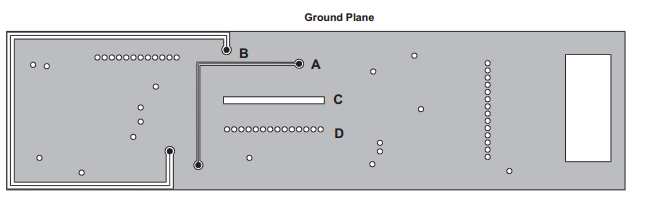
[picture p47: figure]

ECE480 Fall 2012 5 of 9

Figure 2. Shorter trace for capacitor to power

2. Avoid cutting the ground plane. The following figure illustrates a top layer and ground plane. As shown by the letter C, the ground plane has a large slot in it. This creates a large impedance for any voltage difference between the top and bottom of the board. By cutting the holes for the component, more like letter D, the area between the pins allows current to flow. This significantly reduces the impedance of the ground plane. In addition, traces in the ground plane should be avoided whenever possible. When traces in the ground plane are a necessity, avoid making the traces as shown in A. This again cuts the ground plane into left and right sections with a large impedance between the two halves. The letter B shows a much better path, where it goes around the outside of the ground plane. Although this does increase the impedance of trace B, it is better than increasing the impedance of the entire ground plane.

Figure 2. Ground Plane Trace Styles

Low Noise PCB Design

ECE480 Fall 2012 6 of 9

### Avoiding Stray Capacitance

This section will describe two techniques to help reduce the stray capacitance. It is important to be mindful of stray capacitance, which is always present, due to stability and noise issues. Operational amplifiers have stability issues when the input node is capacitive, and will cause oscillation on the output of the amplifier.

1. Keep power lines away from sensitive nodes: Power traces carry a high voltage and the amount of charge on a capacitor is equal to the voltage difference multiplied by capacitance. Although the capacitance will be small due to the physical layout, the potentially large voltage difference between a power trace and signal trace will cause charge to build up. When the signal voltage changes the charge buildup can be injected into the circuit causing noise in the circuit. As shown in Figure 3, the positive and negative power traces go around the circuit to avoid the most critical node, the input node, to the op-amp (circled in yellow).
2. Cut the ground plane: NOTE: This suggestion comes at a price and should only be used when necessary. Since cutting the ground plane increases the impedance of the ground plane, only do it for nodes that are very sensitive to capacitance such as input nodes to an operational amplifier. In Figure 3, the input node to the operational amplifier is circled. As already discussed, inputs to operational amplifiers are particularly sensitive to capacitance which can cause circuit instability. Multi-layer PCB are essentially capacitors, conductive plates separated by an insulator, and therefore every node above the ground plane will have some capacitance. To mitigate this capacitance, the ground plane (and all other planes below or above the node) can be cut, removing the conductive plate that the node would couple with.

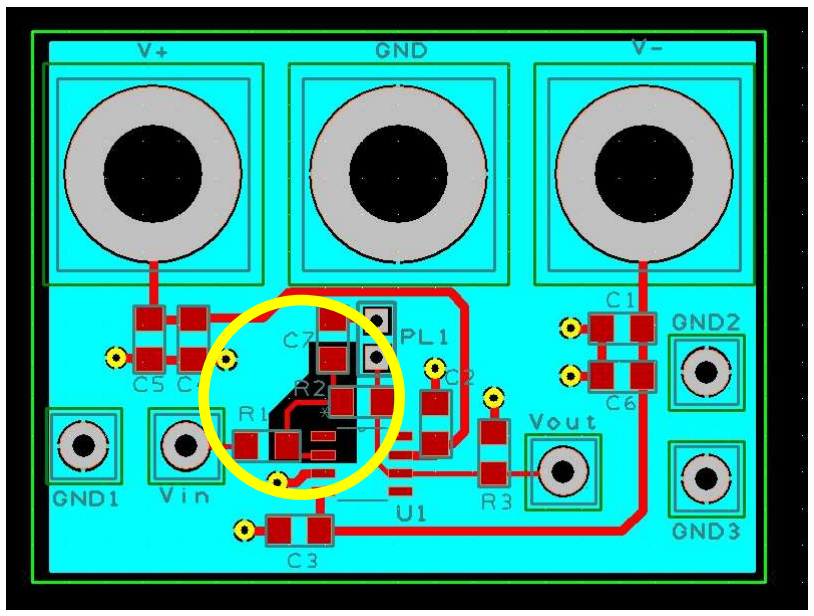
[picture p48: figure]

Figure 3. Sample board design

Low Noise PCB Design

### Avoiding Antennas

It is important to note that according to Texas Instruments, a
for a given frequency. It is given that C = λƒ whe
frequency. This means that as frequency decreases, wavelength increase and there size of an antenna increase. For a frequency of 100M
PCB, the effective wavelength is 75
this large and generally the entire board will be less than 75
board, and typically the traces as well, will not ma
often much longer than 75cm. Any cables
then transfer that noise to the board. Figure 4 show Figure 4, the connectors are on opposite sides of the
different amount of noise to the board, there will
will result in a noisy current traveling through all
part b of Figure 4, where the connectors are right next to each other. the board will be immediately transferred from one c
amount of noisy current that is traveling

ccording to Texas Instruments, an effective antenna
e C is the speed of light, λ is the wavelength and ƒ t as frequency decreases, wavelength increase and there
Hz, a relatively large frequency for circuits on a cm. It is unlikely that any component on a printed circuit board is ire board will be less than 75cm. This means that components on the ke for a good antenna however connecting cables Any cables connected to a printed circuit board can pick up no
two different layouts of connectors on a PCB. In board. This means that if each cable transfers a e a voltage induced across the entire board which of the components. A much better layout is shown in where the connectors are right next to each other. Any voltage that is induced across able to the other and will significantly reduce the traveling through the board.

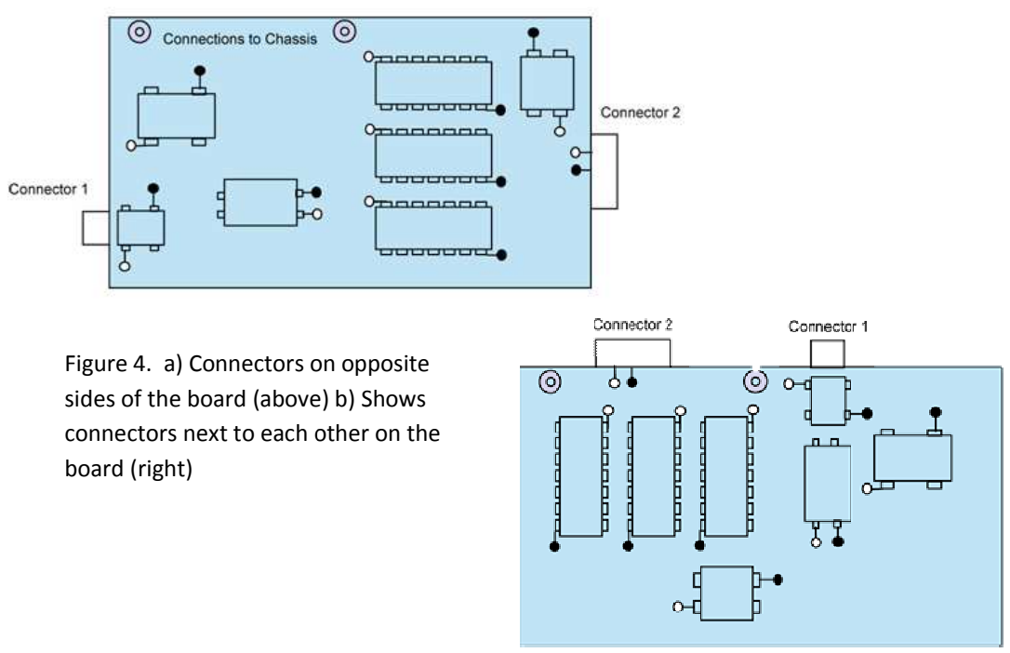
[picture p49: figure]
Figure 4. a) Connectors on opposite; sides of the board (above) b) Shows; connectors next to each other on the; board (right)

ECE480 Fall 2012 7 of 9

trace is at least 1/4 λ
ƒ is the
herefore the effective
a
printed circuit board is

are
ise and
s of connectors on a PCB. In t if each cable transfers a

in
Any voltage that is induced across e

Low Noise PCB Design

ECE480 Fall 2012 8 of 9

## Conclusions and Recommendations

As stated before, it is important to note that these are all suggestions on how to improve performance of a board. Typically there is a trade of for each suggestion so every scenario should be reviewed individually. Reducing noise in one part of the circuit may cost higher impedance elsewhere. Also, sometimes it is not possible to follow some of these guidelines due to design constraints such as size or the complexity of the circuit. Always be mindful of any specifics of the circuit that is being implemented on a PCB and physical constraints such as connectors that have to plug into another board. For active components, the manufacturer will often have a datasheet including some information on where parts should be placed. For example, Texas Instruments points out that for their amplifiers a decoupling capacitor should be placed as close to the power pin of the amplifier as possible. This suggestion from the manufacture would trump moving the capacitor further away to allow a different trace to be shorter.

Low Noise PCB Design

ECE480 Fall 2012 9 of 9

## References

Texas Instruments Guidelines specifically for EMI:

http://www.ti.com/lit/an/szza009/szza009.pdf

Printed Circuit Board Issues – Chapter 12 of Basic Linear Design by Hank Zumbahlen

http://www.analog.com/library/analogdialogue/archives/43-09/EDch%2012%20pc%20issues.pdf

Texas Instruments Presentation on Analog Designs of PCB

http://www.x2y.com/filters/TechDay09kr_hpa_Track2_1_Precision_Analog_Designs_Demand_GoodPCBLayouts%20_JohnWu.pdf

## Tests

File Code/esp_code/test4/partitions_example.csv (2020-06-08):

# Name | Type | SubType | Offset | Size | Flags
# Note: if you have increased the bootloader size | make sure to update the offsets to avoid overlap
nvs | data | nvs | 0x9000 | 0x6000
phy_init | data | phy | 0xf000 | 0x1000
factory | app | factory | 0x10000 | 1M
storage | data | fat |  | 1M

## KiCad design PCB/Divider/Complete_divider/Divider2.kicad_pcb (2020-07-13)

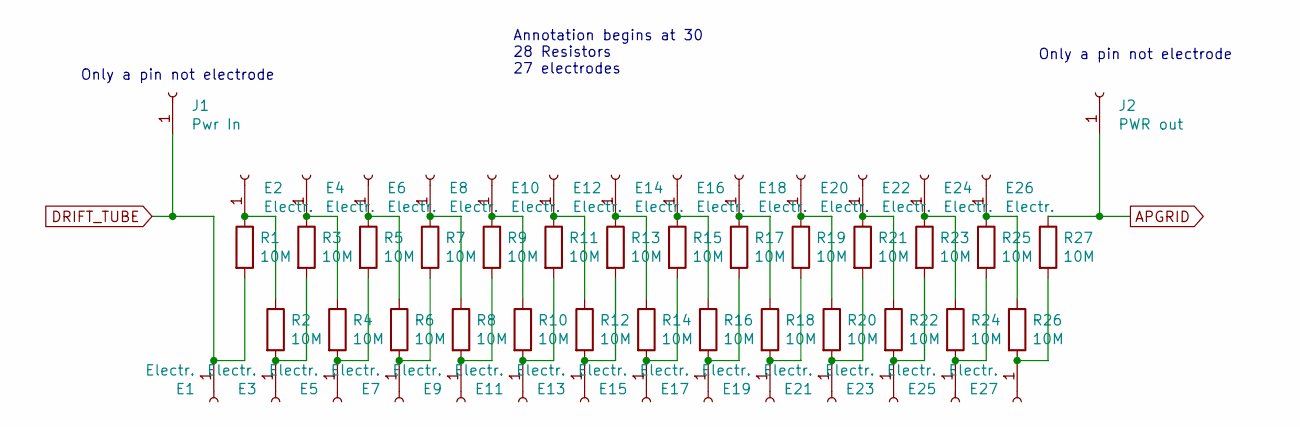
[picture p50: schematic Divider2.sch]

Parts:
E1, E2, E3, E4, E5, E6, E7, E8, E9, E10, E11, E12, E13, E14, E15, E16, E17, E18, E19, E20, E21, E22, E23, E24, E25, E26, E27: Electr.; Pad_for_electrode
J1: Pwr In; Pin_D1.0mm_L10.0mm
J2: PWR out; Pin_D1.0mm_L10.0mm
R1, R2, R3, R4, R5, R6, R7, R8, R9, R10, R11, R12, R13, R14, R15, R16, R17, R18, R19, R20, R21, R22, R23, R24, R25, R26, R27: 10M; R_1206_3216Metric

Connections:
APGRID: J2.1, R27.1
DRIFT_TUBE: E1.1, J1.1, R1.2
unnamed: E2.1, R1.1, R2.1
unnamed: E3.1, R2.2, R3.2
unnamed: E4.1, R3.1, R4.1
unnamed: E5.1, R4.2, R5.2
unnamed: E6.1, R5.1, R6.1
unnamed: E7.1, R6.2, R7.2
unnamed: E8.1, R7.1, R8.1
unnamed: E9.1, R8.2, R9.2
unnamed: E10.1, R9.1, R10.1
unnamed: E11.1, R10.2, R11.2
unnamed: E12.1, R11.1, R12.1
unnamed: E13.1, R12.2, R13.2
unnamed: E14.1, R13.1, R14.1
unnamed: E15.1, R14.2, R15.2
unnamed: E16.1, R15.1, R16.1
unnamed: E17.1, R16.2, R17.2
unnamed: E18.1, R17.1, R18.1
unnamed: E19.1, R18.2, R19.2
unnamed: E20.1, R19.1, R20.1
unnamed: E21.1, R20.2, R21.2
unnamed: E22.1, R21.1, R22.1
unnamed: E23.1, R22.2, R23.2
unnamed: E24.1, R23.1, R24.1
unnamed: E25.1, R24.2, R25.2
unnamed: E26.1, R25.1, R26.1
unnamed: E27.1, R26.2, R27.2

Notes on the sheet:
Annotation begins at 30 28 Resistors 27 electrodes
Only a pin not electrode

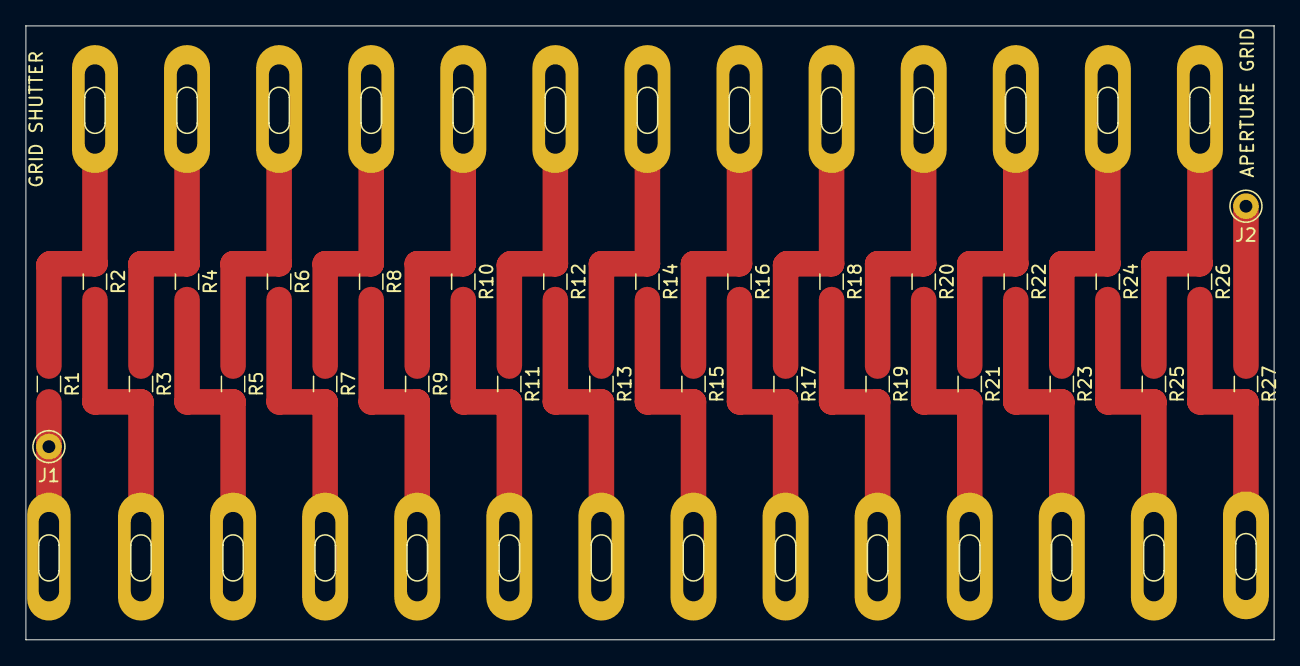
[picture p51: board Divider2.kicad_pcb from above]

Board: 2 copper layers, 97.6 x 48.0 mm, 56 parts (0 on the bottom side), 28 nets.

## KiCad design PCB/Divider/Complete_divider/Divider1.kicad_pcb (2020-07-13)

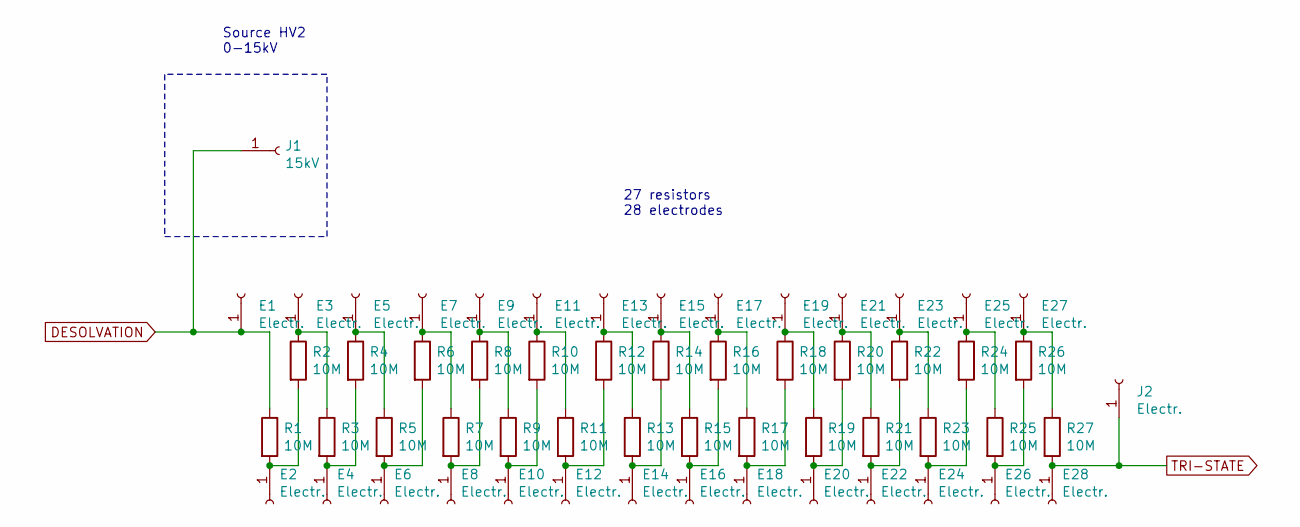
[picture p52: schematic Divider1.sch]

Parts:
E1, E2, E3, E4, E5, E6, E7, E8, E9, E10, E11, E12, E13, E14, E15, E16, E17, E18, E19, E20, E21, E22, E23, E24, E25, E26, E27, E28: Electr.; Pad_for_electrode
J1: 15kV; Pin_D1.4mm_L8.5mm_W2.8mm_FlatFork
J2: Electr.; Pin_D1.0mm_L10.0mm
R1, R2, R3, R4, R5, R6, R7, R8, R9, R10, R11, R12, R13, R14, R15, R16, R17, R18, R19, R20, R21, R22, R23, R24, R25, R26, R27: 10M; R_1206_3216Metric_Pad1.42x1.75mm_HandSolder

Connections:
DESOLVATION: E1.1, J1.1, R1.1
unnamed: E2.1, R1.2, R2.2
unnamed: E3.1, R2.1, R3.1
unnamed: E4.1, R3.2, R4.2
unnamed: E5.1, R4.1, R5.1
unnamed: E6.1, R5.2, R6.2
unnamed: E7.1, R6.1, R7.1
unnamed: E8.1, R7.2, R8.2
unnamed: E9.1, R8.1, R9.1
unnamed: E10.1, R9.2, R10.2
unnamed: E11.1, R10.1, R11.1
unnamed: E12.1, R11.2, R12.2
unnamed: E13.1, R12.1, R13.1
unnamed: E14.1, R13.2, R14.2
unnamed: E15.1, R14.1, R15.1
unnamed: E16.1, R15.2, R16.2
unnamed: E17.1, R16.1, R17.1
unnamed: E18.1, R17.2, R18.2
unnamed: E19.1, R18.1, R19.1
unnamed: E20.1, R19.2, R20.2
unnamed: E21.1, R20.1, R21.1
unnamed: E22.1, R21.2, R22.2
unnamed: E23.1, R22.1, R23.1
unnamed: E24.1, R23.2, R24.2
unnamed: E25.1, R24.1, R25.1
unnamed: E26.1, R25.2, R26.2
unnamed: E27.1, R26.1, R27.1
TRI-STATE: E28.1, J2.1, R27.2

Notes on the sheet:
Source HV2 0-15kV
27 resistors 28 electrodes

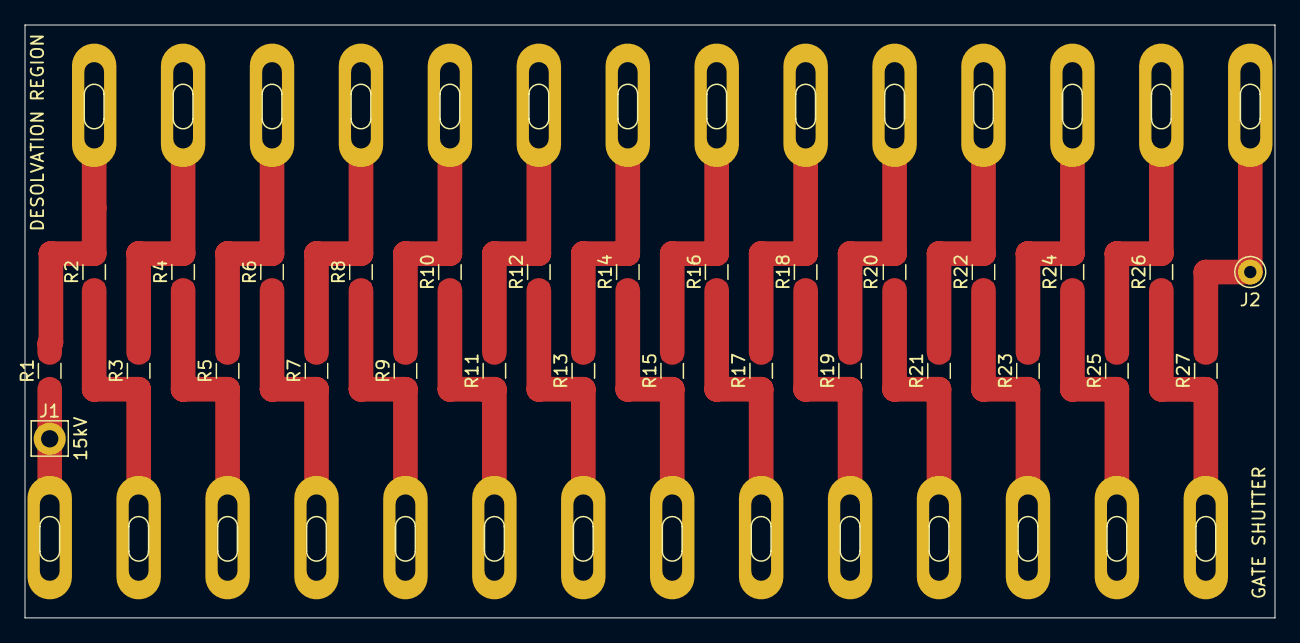
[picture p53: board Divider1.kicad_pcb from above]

Board: 2 copper layers, 101.2 x 48.0 mm, 57 parts (0 on the bottom side), 28 nets.

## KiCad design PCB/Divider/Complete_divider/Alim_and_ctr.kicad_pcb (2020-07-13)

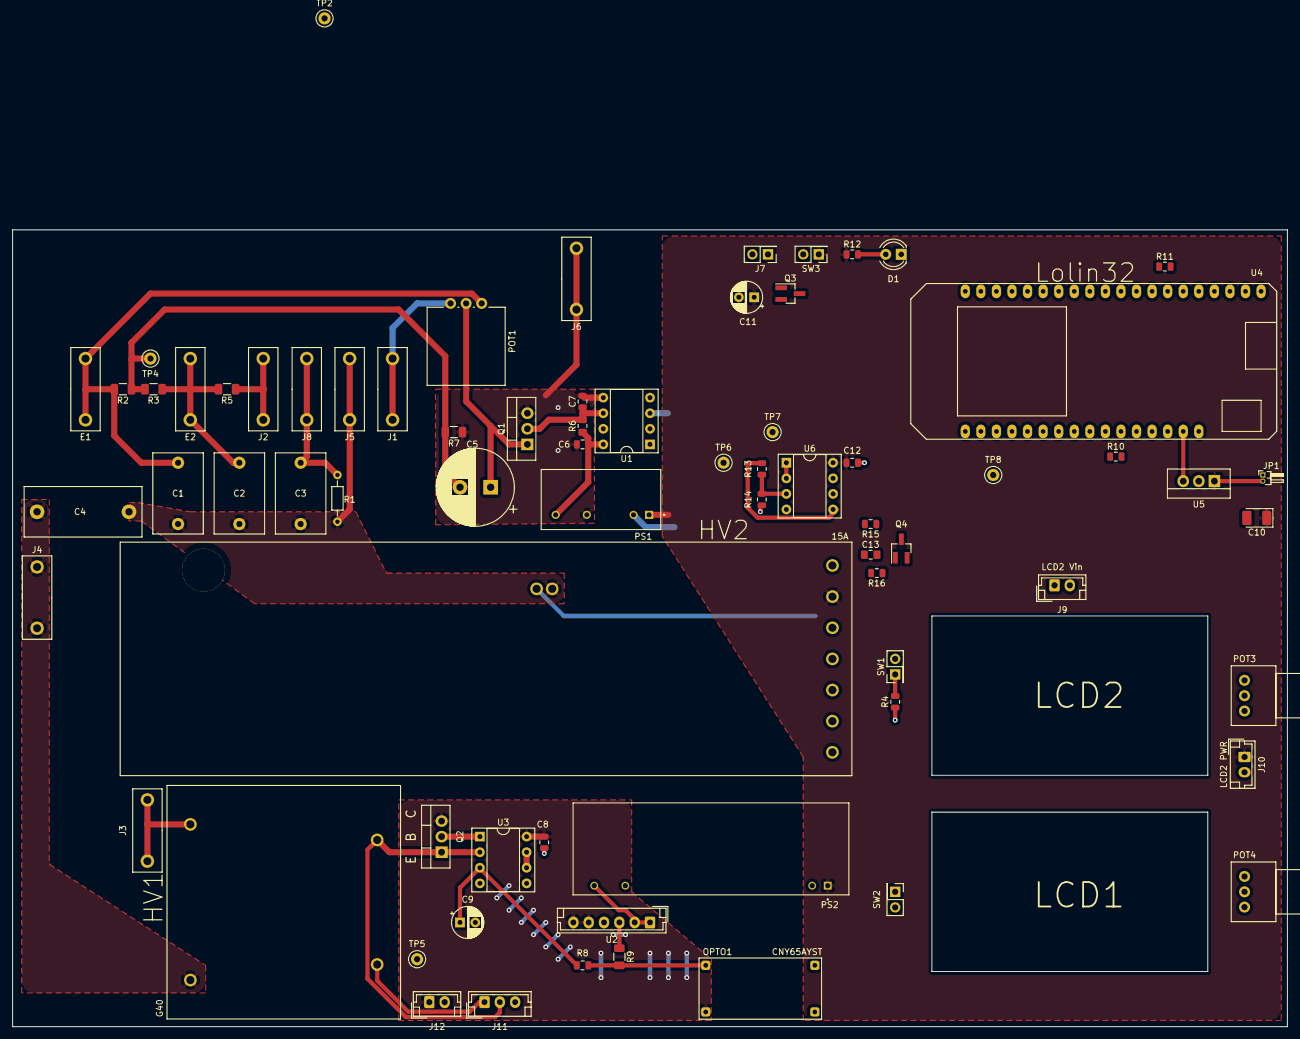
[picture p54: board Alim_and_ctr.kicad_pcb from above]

Board: 2 copper layers, 208.0 x 130.0 mm, 72 parts (0 on the bottom side), 47 nets.

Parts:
C1, C2: 4700pF 10kV; C_Rect_L13.0mm_W8.0mm_P10.00mm_FKS3_FKP3_MKS4
C3: 0.22uF; C_Rect_L13.0mm_W8.0mm_P10.00mm_FKS3_FKP3_MKS4
C4: 2500pF 15 kV; C_Rect_L19.0mm_W8.0mm_P15.00mm_MKS4
C5: 47uF/100V; CP_Radial_D12.5mm_P5.00mm
C6, C8, C12: 100nF; C_0805_2012Metric
C7: 15pF; C_0805_2012Metric
C9: 2,2uF; CP_Radial_D5.0mm_P2.50mm
C10: 0.33uF Tant.; CP_EIA-3528-21_Kemet-B_Pad1.50x2.35mm_HandSolder
C11: 100uF; CP_Radial_D5.0mm_P2.50mm
C13: 2,2uF; C_0805_2012Metric_Pad1.15x1.40mm_HandSolder
D1: PWR LED; LED_D4.0mm
E1: Mid electrode1; conn_HV_JACK_PB1021
E2: Mid electrode2; conn_HV_JACK_PB1021
HV1: G40
HV2: 15A
J1: Electrode in; conn_HV_JACK_PB1021
J2: Electrode out; conn_HV_JACK_PB1021
J3, J4: HV out; conn_HV_JACK_PB1021
J5: Last Electrode; conn_HV_JACK_PB1021
J6: Gate; conn_HV_JACK_PB1021
J7: 12V in; PinHeader_2x01_P2.54mm_Vertical
J8: Ap Grid; conn_HV_JACK_PB1021
J9: LCD2 Vin; JST_EH_B2B-EH-A_1x02_P2.50mm_Vertical
J10: LCD2 PWR; JST_EH_B2B-EH-A_1x02_P2.50mm_Vertical
J11: LCD1 V/I measures; JST_EH_B3B-EH-A_1x03_P2.50mm_Vertical
J12: LCD1 PWR; JST_EH_B2B-EH-A_1x02_P2.50mm_Vertical
JP1: Jumper; PinHeader_1x02_P1.00mm_Horizontal
OPTO1: CNY65AYST
POT1: 10M; Potentiometer_Vishay_148-149_Single_Vertical
POT3, POT4: 50K; Potentiometer_Alps_RK097_Single_Horizontal
PS1: RHV2-1212S/R20; R8
PS2: RHV2-1212S/R20; R20
Q1: ZVN2110A; TO-220-3_Vertical
Q2: ZTX1053A; TO-220-3_Vertical
Q3: SSM3J340R; SOT-23_Handsoldering
Q4: ZTX1053A; SOT-23_Handsoldering
R1: 500K; R_Axial_DIN0204_L3.6mm_D1.6mm_P7.62mm_Horizontal
R2, R3: 1.5M; R_1206_3216Metric
R4, R14: 1M; R_0805_2012Metric
R5: 10M; R_1206_3216Metric
R6: 5K; R_0805_2012Metric_Pad1.15x1.40mm_HandSolder
R7: 50R; R_1206_3216Metric
R8, R15, R16: 20K; R_0805_2012Metric
R9: 1K; R_1206_3216Metric
R10, R11: 100R; R_0805_2012Metric
R12: R_LED; R_0805_2012Metric
R13: 3.3M; R_0805_2012Metric
SW1: EN switch; PinHeader_2x01_P2.54mm_Vertical
SW2: HV1 Switch; PinHeader_2x01_P2.54mm_Vertical
SW3: PWR switch; PinHeader_2x01_P2.54mm_Vertical
TP2, TP4, TP5, TP6, TP7, TP8: TestPoint; TestPoint_Keystone_5000-5004_Miniature
U1: 6N137A; DIP-8_W7.62mm_Socket
U2: mEZD41501A-X; JST_EH_B6B-EH-A_1x06_P2.50mm_Vertical
U3: LM358; DIP-8_W7.62mm_Socket
U4: Lolin32
U5: MC78M15ACTG; TO-262-3_Vertical
U6: LM358P; DIP-8_W7.62mm_Socket

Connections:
+3V3: POT3.1, POT4.1, U4.1, U4.20
+5V: JP1.1, Q4.3, U5.3
+12V: C10.1, C11.1, C12.2, HV2.2, J10.1, PS1.1, PS2.1, R12.1, SW3.1, U5.1, U6.8
+12VA: C6.1, PS1.4, R6.1, U1.8
+15V: C8.1, J12.1, OPTO1.4, Q2.3, U2.5, U2.6, U3.8
/Aperture_Grid: C3.1, J8.1, R1.1
/Middle_electrode1: C1.1, E1.1, POT1.3, R2.2
/Middle_electrode2: C2.1, E2.1, R3.1, R5.2
ADC1: POT3.2, U4.6
ADC2: POT4.2, U4.7
ADJ_HV2: C13.1, HV2.6, R15.2
ADJ_HV2_PWM: Q4.2, U4.5
ALIMHV1+: HV1.1, J11.2, Q2.1, TP5.1, U3.2
ALIMHV1-: HV1.2, J11.1
COUNTER_ELECTRODE: C4.1, HV1.4, HV2.10, J4.1
DRIFT_TUBE: J2.1, R5.1
EOUT: HV2.9, R13.1, TP6.1, U6.5
EOUTPIN: TP8.1, U4.8, U6.1, U6.2
GATE_IN+: C5.1, POT1.2, Q1.1, TP2.1
GATE_IN-: C5.2, R2.1, R3.2, R7.2, TP4.1
GATE_OUT: C6.2, C7.2, J6.1, PS1.3, Q1.3, R7.1, U1.5
GND: C10.2, C11.2, C12.1, C13.2, D1.1, HV2.1, J7.2, J9.2, J10.2, OPTO1.2, POT3.3, POT4.3, PS1.2, PS2.2, Q3.2, R4.1, R14.2, R16.2, U1.3, U4.16, U4.17, U4.23, U4.24, U4.34, U5.2, U6.4, U6.6
GNDB: C8.2, C9.2, J11.3, J12.2, PS2.3, R9.1, U2.3, U2.4, U3.4, U3.5
GRID_CTRL: R10.1, U1.2
IOUT: HV2.3, U4.13
LAST_ELECTRODE: C1.2, C2.2, C3.2, C4.2, HV2.8, J5.1, R1.2
LCD2_MEASURE: J9.1, U6.7
NEEDLE: HV1.3, J3.1
unnamed: C7.1, Q1.2, R6.2, U1.6
unnamed: C9.1, R8.2, U3.3
unnamed: D1.2, R12.2
unnamed: HV2.4, SW1.2
unnamed: J7.1, Q3.1
unnamed: JP1.2, U4.15
unnamed: OPTO1.3, R8.1, R9.2
unnamed: PS2.4, U2.1, U2.2
unnamed: Q2.2, U3.1
unnamed: Q3.3, SW3.2
unnamed: Q4.1, R15.1, R16.1
unnamed: R4.2, SW1.1
unnamed: R10.2, U4.11
unnamed: R11.1, SW2.1
unnamed: R11.2, U4.30
unnamed: R13.2, R14.1, TP7.1, U6.3
unnamed: U3.6, U3.7
PWM: OPTO1.1, SW2.2
TRI-STATE: J1.1, POT1.1

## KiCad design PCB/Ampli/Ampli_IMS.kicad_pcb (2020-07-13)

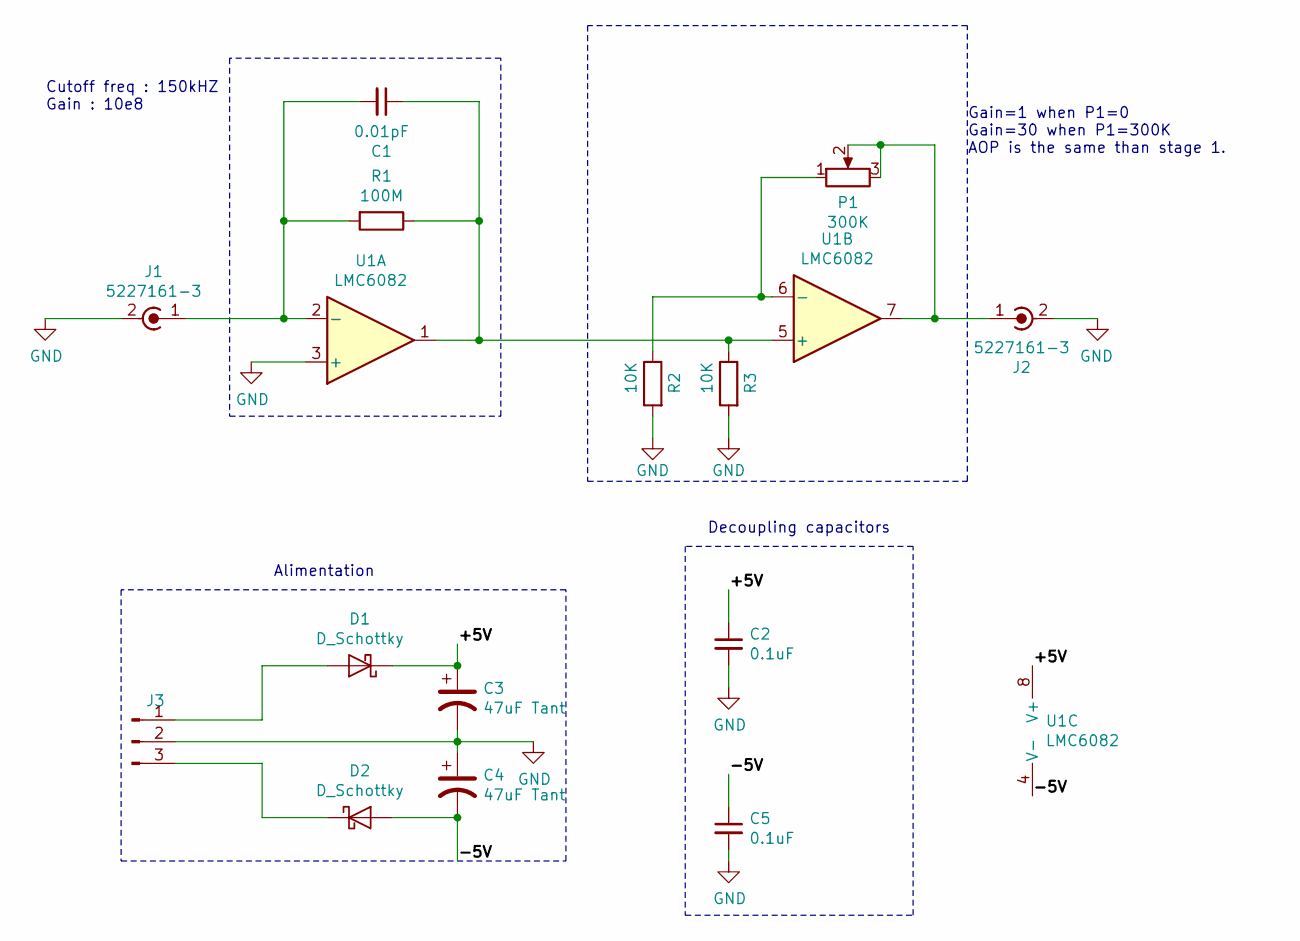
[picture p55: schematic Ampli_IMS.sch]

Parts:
C1: 0.01pF; C_0805_2012Metric
C2, C5: 0.1uF; C_0805_2012Metric; LCSC C360619
C3, C4: 47uF Tant; CP_EIA-3216-18_Kemet-A_Pad1.58x1.35mm_HandSolder; LCSC C139817
D1, D2: D_Schottky; D_0805_2012Metric_Castellated; LCSC MSCD104H
J1: 5227161-3; SMA_Amphenol_132203-12_Horizontal; LCSC MOUSER
J2: 5227161-3; BNC_Amphenol_B6252HB-NPP3G-50_Horizontal
J3: Conn_01x03_Male; JST_EH_B3B-EH-A_1x03_P2.50mm_Vertical; LCSC MOUSER
P1: 300K; Potentiometer_Alps_RK09Y11_Single_Horizontal
R1: 100M; C_0805_2012Metric
R2, R3: 10K; C_0805_2012Metric
U1: LMC6082; SO-8_3.9x4.9mm_P1.27mm; LCSC MOUSER

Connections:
/+5V: C2.1, C3.1, D1.1 (K), U1.8 (V+)
/-5V: C4.2, C5.1, D2.2 (A), U1.4 (V-)
GND: C2.2, C3.2, C4.1, C5.2, J1.2 (Ext), J2.2 (Ext), J3.2, R2.2, R3.2, U1.3 (+)
unnamed: C1.1, R1.1, R3.1, U1.1, U1.5 (+)
unnamed: C1.2, J1.1 (In), R1.2, U1.2 (-)
unnamed: D1.2 (A), J3.1
unnamed: D2.1 (K), J3.3
unnamed: J2.1 (In), P1.2, P1.3, U1.7
unnamed: P1.1, R2.1, U1.6 (-)

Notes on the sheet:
Decoupling capacitors
Alimentation
Gain=1 when P1=0 Gain=30 when P1=300K AOP is the same than stage 1.
Cutoff freq : 150kHZ Gain : 10e8

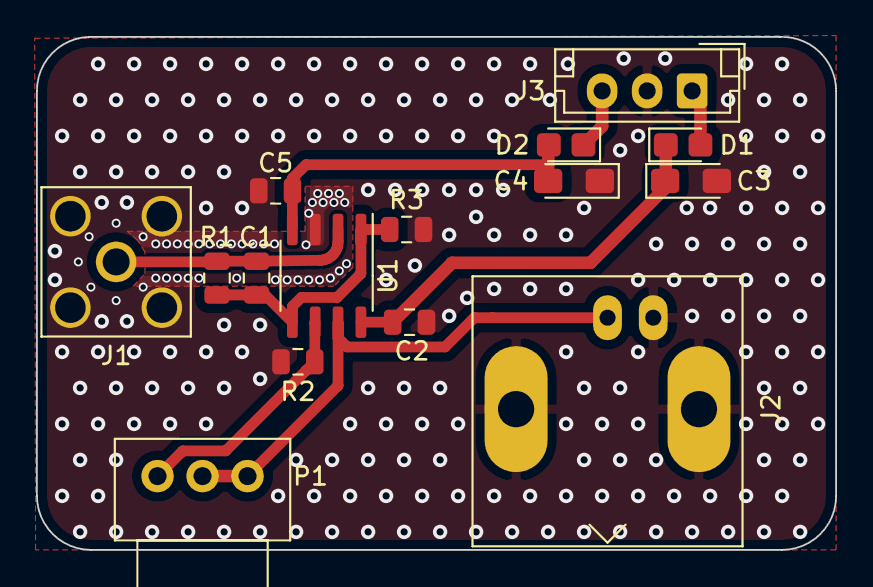
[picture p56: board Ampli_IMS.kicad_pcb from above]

Board: 2 copper layers, 44.4 x 28.5 mm, 15 parts (0 on the bottom side), 9 nets.

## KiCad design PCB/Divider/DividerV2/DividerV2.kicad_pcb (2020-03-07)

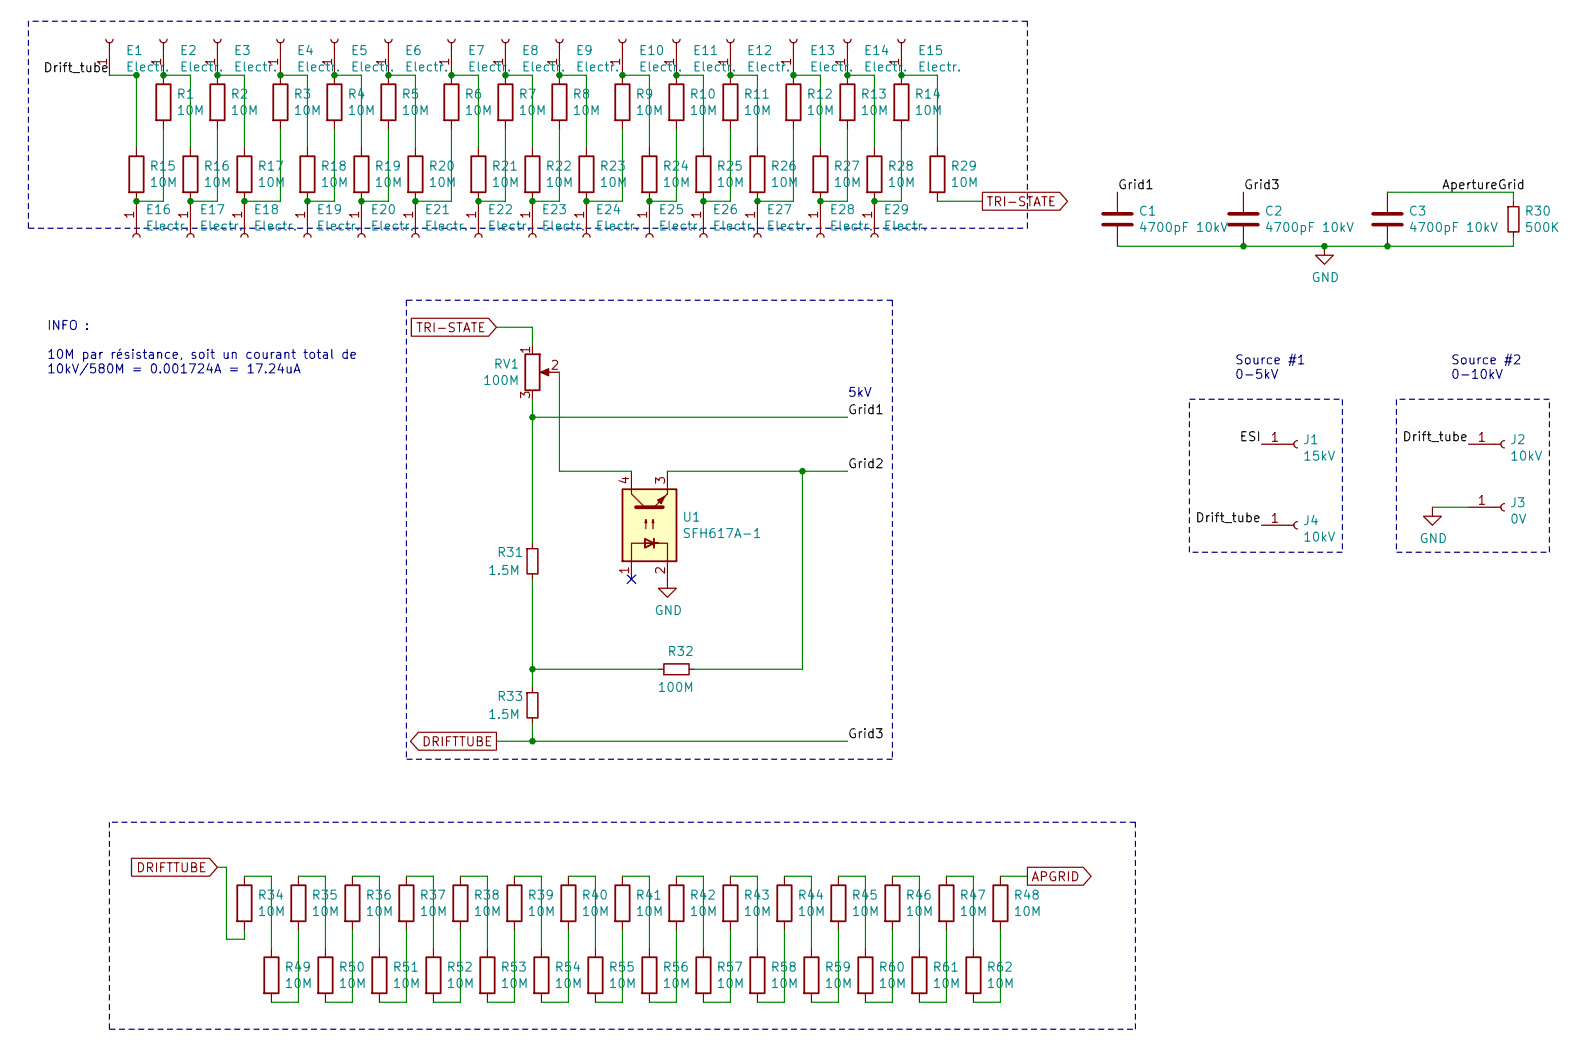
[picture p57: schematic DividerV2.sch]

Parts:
C1, C2, C3: 4700pF 10kV; C_Rect_L13.0mm_W8.0mm_P10.00mm_FKS3_FKP3_MKS4
E1, E2, E3, E4, E5, E6, E7, E8, E9, E10, E11, E12, E13, E14, E15, E16, E17, E18, E19, E20, E21, E22, E23, E24, E25, E26, E27, E28, E29: Electr.; Pad_for_electrode
J1: 15kV; Pin_D1.4mm_L8.5mm_W2.8mm_FlatFork
J2, J4: 10kV; Pin_D1.4mm_L8.5mm_W2.8mm_FlatFork
J3: 0V; Pin_D1.4mm_L8.5mm_W2.8mm_FlatFork
R1, R2, R3, R4, R5, R6, R7, R8, R9, R10, R11, R12, R13, R14, R15, R16, R17, R18, R19, R20, R21, R22, R23, R24, R25, R26, R27, R28, R29: 10M; R_1206_3216Metric_Pad1.42x1.75mm_HandSolder
R30: 500K; R_Axial_DIN0207_L6.3mm_D2.5mm_P15.24mm_Horizontal
R31, R33: 1.5M; R_1206_3216Metric
R32: 100M; R_1206_3216Metric
R34, R35, R36, R37, R38, R39, R40, R41, R42, R43, R44, R45, R46, R47, R48, R49, R50, R51, R52, R53, R54, R55, R56, R57, R58, R59, R60, R61, R62: 10M; R_1206_3216Metric
RV1: 100M; Potentiometer_ACP_CA14-H4_Horizontal
U1: SFH617A-1; DIP-4_W7.62mm

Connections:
/ApertureGrid: C3.1, R30.1
/Drift_tube: E1.1, J2.1, J4.1, R15.1
/ESI: J1.1
/Grid1: C1.1, R31.1, RV1.3
/Grid2: R32.2, U1.3
APGRID: R48.1
DRIFTTUBE: C2.1, R33.2, R34.2
GND: C1.2, C2.2, C3.2, J3.1, R30.2, U1.2
unnamed: E2.1, R1.1, R16.1
unnamed: E3.1, R2.1, R17.1
unnamed: E4.1, R3.1, R18.1
unnamed: E5.1, R4.1, R19.1
unnamed: E6.1, R5.1, R20.1
unnamed: E7.1, R6.1, R21.1
unnamed: E8.1, R7.1, R22.1
unnamed: E9.1, R8.1, R23.1
unnamed: E10.1, R9.1, R24.1
unnamed: E11.1, R10.1, R25.1
unnamed: E12.1, R11.1, R26.1
unnamed: E13.1, R12.1, R27.1
unnamed: E14.1, R13.1, R28.1
unnamed: E15.1, R14.1, R29.1
unnamed: E16.1, R1.2, R15.2
unnamed: E17.1, R2.2, R16.2
unnamed: E18.1, R3.2, R17.2
unnamed: E19.1, R4.2, R18.2
unnamed: E20.1, R5.2, R19.2
unnamed: E21.1, R6.2, R20.2
unnamed: E22.1, R7.2, R21.2
unnamed: E23.1, R8.2, R22.2
unnamed: E24.1, R9.2, R23.2
unnamed: E25.1, R10.2, R24.2
unnamed: E26.1, R11.2, R25.2
unnamed: E27.1, R12.2, R26.2
unnamed: E28.1, R13.2, R27.2
unnamed: E29.1, R14.2, R28.2
unnamed: R31.2, R32.1, R33.1
unnamed: R34.1, R49.1
unnamed: R35.1, R50.1
unnamed: R35.2, R49.2
unnamed: R36.1, R51.1
unnamed: R36.2, R50.2
unnamed: R37.1, R52.1
unnamed: R37.2, R51.2
unnamed: R38.1, R53.1
unnamed: R38.2, R52.2
unnamed: R39.1, R54.1
unnamed: R39.2, R53.2
unnamed: R40.1, R55.1
unnamed: R40.2, R54.2
unnamed: R41.1, R56.1
unnamed: R41.2, R55.2
unnamed: R42.1, R57.1
unnamed: R42.2, R56.2
unnamed: R43.1, R58.1
unnamed: R43.2, R57.2
unnamed: R44.1, R59.1
unnamed: R44.2, R58.2
unnamed: R45.1, R60.1
unnamed: R45.2, R59.2
unnamed: R46.1, R61.1
unnamed: R46.2, R60.2
unnamed: R47.1, R62.1
unnamed: R47.2, R61.2
unnamed: R48.2, R62.2
unnamed: RV1.2, U1.4
TRI-STATE: R29.2, RV1.1

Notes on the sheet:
5kV
INFO : 10M par résistance, soit un courant total de 10kV/580M = 0.001724A = 17.24uA
Source #2 0-10kV
Source #1 0-5kV

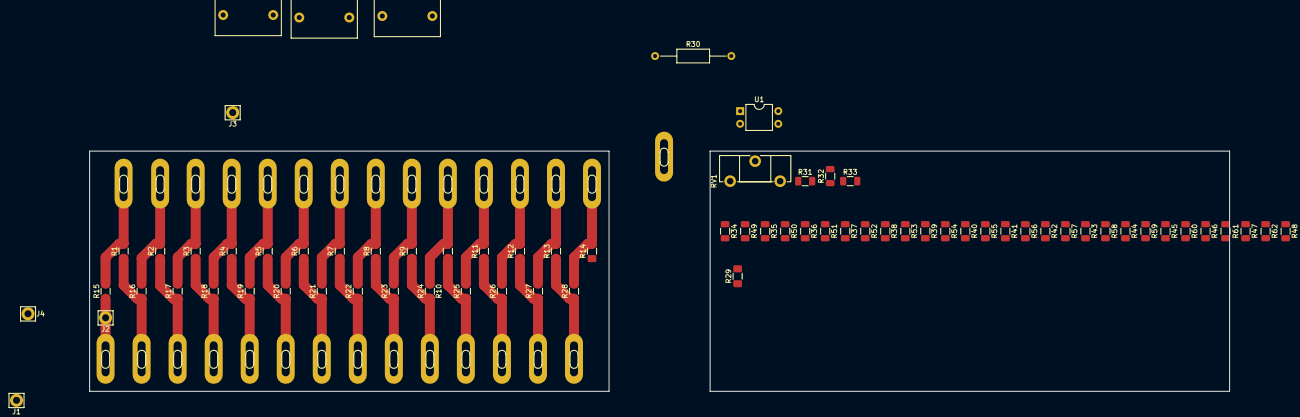
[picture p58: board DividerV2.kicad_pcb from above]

Board: 2 copper layers, 227.8 x 48.0 mm, 100 parts (0 on the bottom side), 65 nets.

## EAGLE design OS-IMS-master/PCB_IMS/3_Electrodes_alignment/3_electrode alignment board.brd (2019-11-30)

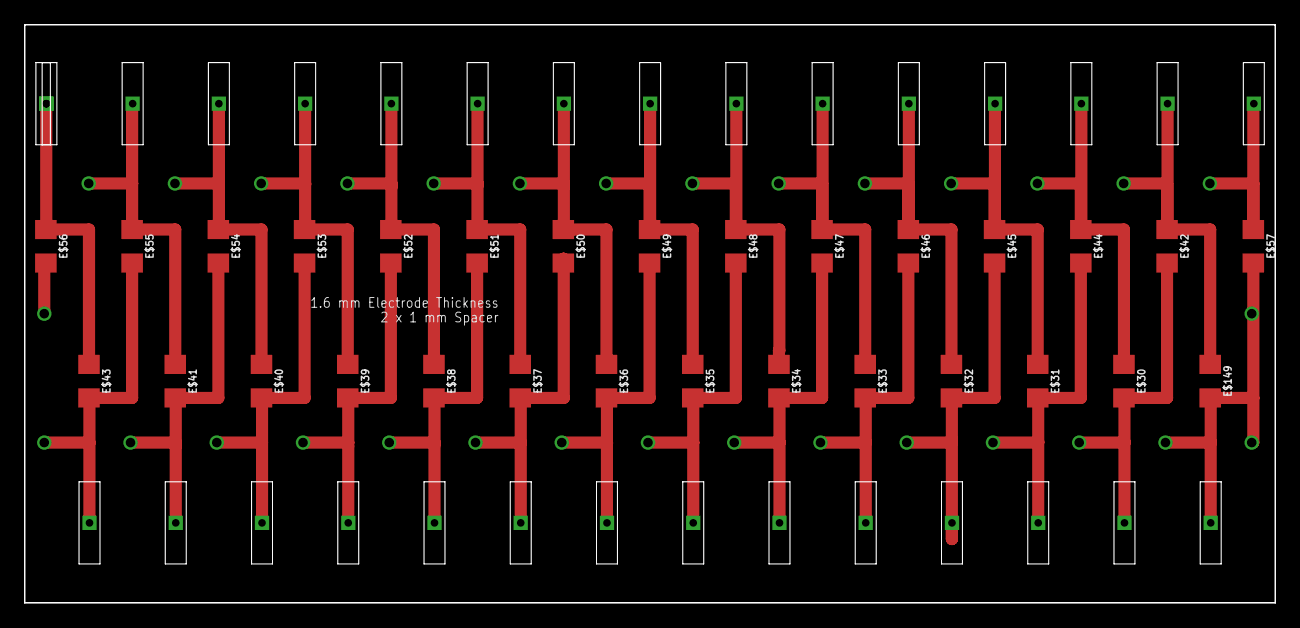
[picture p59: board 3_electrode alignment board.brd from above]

Board: 2 copper layers, 104.4 x 48.3 mm, 59 parts (0 on the bottom side), 3 nets.

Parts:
E$1, E$2, E$3, E$4, E$5, E$6, E$7, E$8, E$9, E$10, E$11, E$12, E$13, E$14, E$15, E$16, E$17, E$18, E$19, E$20, E$21, E$22, E$23, E$24, E$25, E$26, E$27, E$28, E$29: SLOT2
E$30, E$31, E$32, E$33, E$34, E$35, E$36, E$37, E$38, E$39, E$40, E$41, E$42, E$43, E$44, E$45, E$46, E$47, E$48, E$49, E$50, E$51, E$52, E$53, E$54, E$55, E$56, E$57, E$149: 1206
E$222: SLOT1

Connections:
S$1: E$43.1, E$56.1, E$222.P$1
S$11: E$2.P$1, E$16.P$1, E$17.P$1, E$18.P$1, E$19.P$1, E$20.P$1, E$21.P$1, E$22.P$1, E$23.P$1, E$24.P$1, E$25.P$1, E$26.P$1, E$27.P$1, E$28.P$1, E$30.2, E$31.2, E$32.2, E$33.2, E$34.2, E$35.2, E$36.2, E$37.2, E$38.2, E$39.2, E$40.2, E$41.2, E$42.2, E$43.2, E$44.2, E$45.2, E$46.2, E$47.2, E$48.2, E$49.2, E$50.2, E$51.2, E$52.2, E$53.2, E$54.2, E$55.2, E$57.2, E$149.2
S$12: E$3.P$1, E$4.P$1, E$5.P$1, E$6.P$1, E$7.P$1, E$8.P$1, E$9.P$1, E$10.P$1, E$11.P$1, E$12.P$1, E$13.P$1, E$14.P$1, E$15.P$1, E$29.P$1, E$30.1, E$31.1, E$32.1, E$33.1, E$34.1, E$35.1, E$36.1, E$37.1, E$38.1, E$39.1, E$40.1, E$41.1, E$42.1, E$44.1, E$45.1, E$46.1, E$47.1, E$48.1, E$49.1, E$50.1, E$51.1, E$52.1, E$53.1, E$54.1, E$55.1, E$57.1, E$149.1

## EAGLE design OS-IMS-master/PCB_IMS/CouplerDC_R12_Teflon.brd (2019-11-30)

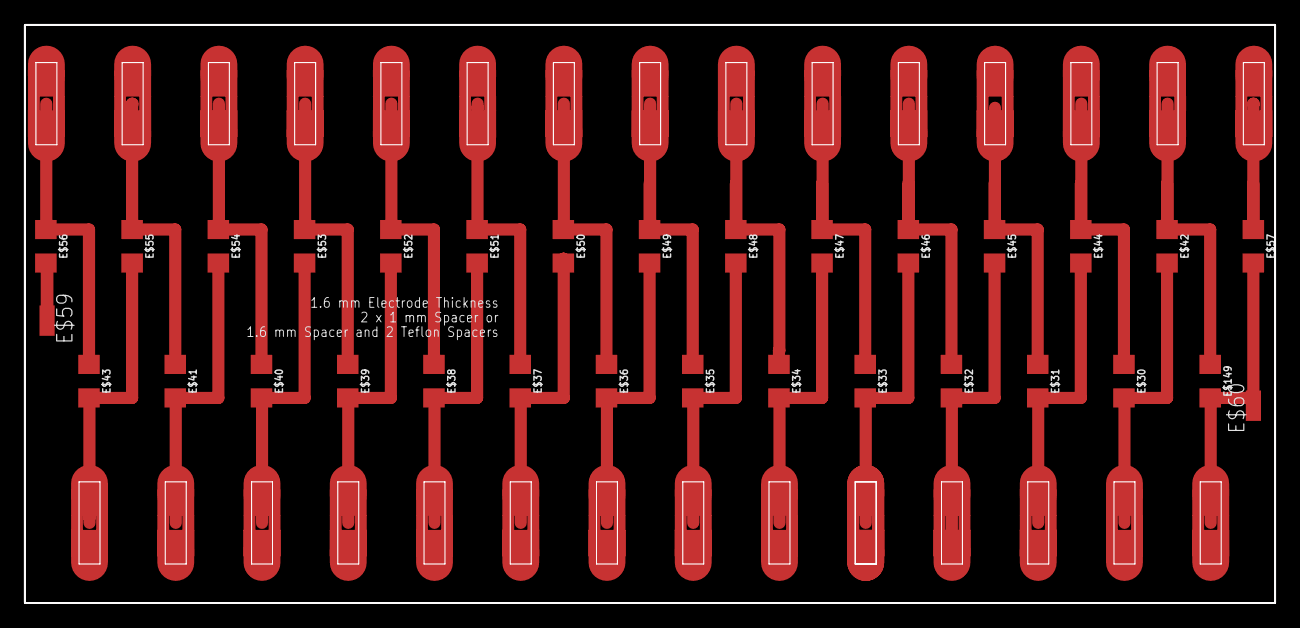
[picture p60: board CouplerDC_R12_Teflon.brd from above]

Board: 2 copper layers, 104.4 x 48.3 mm, 61 parts (0 on the bottom side), 28 nets.

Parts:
E$1, E$2, E$3, E$4, E$5, E$6, E$7, E$8, E$9, E$10, E$11, E$12, E$13, E$14, E$15, E$16, E$17, E$18, E$19, E$20, E$21, E$22, E$23, E$24, E$25, E$26, E$27, E$28, E$29, E$58: GAAEXTENSIONS_SLOT3
E$30, E$31, E$32, E$33, E$34, E$35, E$36, E$37, E$38, E$39, E$40, E$41, E$42, E$43, E$44, E$45, E$46, E$47, E$48, E$49, E$50, E$51, E$52, E$53, E$54, E$55, E$56, E$57, E$149: 1206
E$59, E$60: SMD1,27-2,54

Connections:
S$1: E$43.1, E$56.1
S$11: E$57.2, E$149.2
S$12: E$36.1, E$50.1
S$14: E$41.1, E$55.1
S$15: E$40.1, E$54.1
S$16: E$39.1, E$53.1
S$17: E$38.1, E$52.1
S$18: E$41.2, E$54.2
S$19: E$39.2, E$52.2
S$20: E$40.2, E$53.2
S$21: E$43.2, E$55.2
S$22: E$38.2, E$51.2
S$23: E$37.2, E$50.2
S$36: E$36.2, E$49.2
S$38: E$35.2, E$48.2
S$39: E$34.2, E$47.2
S$40: E$33.2, E$46.2
S$41: E$32.2, E$45.2
S$42: E$31.2, E$44.2
S$43: E$30.2, E$42.2
S$45: E$42.1, E$149.1
S$46: E$30.1, E$44.1
S$47: E$31.1, E$45.1
S$48: E$32.1, E$46.1
S$49: E$33.1, E$47.1
S$50: E$34.1, E$48.1
S$52: E$35.1, E$49.1
S$53: E$37.1, E$51.1

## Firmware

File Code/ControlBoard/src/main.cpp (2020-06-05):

#include <Arduino.h>
#include <Wire.h>

#define PWM_FREQ 1000
#define PWM_PIN 16
#define PWM_CHANNEL 0
#define PWM_RES 8

#define EOUT_MEASURE_PIN 12
#define IOUT_MEASURE_PIN 13






void setup(){
  // configure LED PWM functionalitites
  ledcSetup(PWM_CHANNEL, PWM_FREQ, PWM_RES);
  ledcSetup(1, PWM_FREQ, PWM_RES);
  // attach the channel to the GPIO to be controlled
  ledcAttachPin(PWM_PIN, PWM_CHANNEL);
  ledcAttachPin(LED_BUILTIN, 1);

  //pinMode(EOUT_MEASURE_PIN,INPUT);
  pinMode(IOUT_MEASURE_PIN,INPUT);

  Serial.begin(115200);

}
 
bool asked = 0;  //asked=0 => nothing has been asked to the user
char tab[16];
int DutyCycle = 0;
int HVToReach = 0;
double voltage_applied =0;


int ReadMonitor(){
  for(int i =0;i<16;i++){
      tab[i]=0;
    }
  Serial.readBytesUntil('\n', tab, 15); // put the characters into the tab 

  return atoi(tab);                // convert str into int
}


void SearchForCharacters(){

  if(Serial.available()>0){

    int HV_asked = ReadMonitor();
    voltage_applied = HV_asked;
    //voltage_applied = (HV_asked+193.64)/332.27;  ////////////////

    if(HV_asked>15 || HV_asked<0){           // ERROR : serial character invalid
      Serial.println("Error : HV must be in the range 0 to 15");
      voltage_applied = 0;
      asked = 0; 
      return;
    }

    else{
      Serial.print("You have asked a voltage of ");
      Serial.print(HV_asked);   
      Serial.print("V, hence ");
      Serial.println(voltage_applied);
      asked = 0; 
      return;
    }
  }

  else {
    return;     //nothing to update
  }
}


void MeasureVoltage(){
  static int count =0;
  static float eout = 0.0;

  while(count<100){
    float a = (float)analogRead(EOUT_MEASURE_PIN);
    //Serial.println(a);
    
    eout = eout + a*3.3*4.3/4095+0.6;          //4.3 : divider ratio with R1=3.3M and R2=1M. 
                                //1.18 : to set the measure to maximum when the input is 12V
    count++;
  }
  
  Serial.print("The achieved voltage is ");
  Serial.print(eout/100);
  Serial.println("Volts");
  count=0;
  eout=0;
}


void loop(){

  
  
  if (!asked){
    // Serial.println("1 : Set voltage on HV1 \n 2 : Read voltage on HV2 \n 3 : Read current on HV2 ");
    Serial.println("HV to reach in Volts SVP?");
    asked=1;
  }

  if(asked){
    SearchForCharacters();
    DutyCycle = voltage_applied*255/15;    //calculate duty cycle
  }

  ledcWrite(PWM_CHANNEL,DutyCycle);
  ledcWrite(1, DutyCycle); 
  delay(1000); 
  //MeasureVoltage();
}

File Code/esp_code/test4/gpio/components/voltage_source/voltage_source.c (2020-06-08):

#include <stdio.h>
#include "freertos/FreeRTOS.h"
#include "freertos/task.h"
#include "driver/ledc.h"
#include "esp_err.h"



#include "voltage_source.h"
#include "cmd_system.h"

void TaskVoltage15K( void *pvParameters );
void TaskVoltage4K( void *pvParameters );

void start_TaskVoltage15K()
{
    xTaskCreatePinnedToCore(
        TaskVoltage15K
        ,  "Voltage15K"   // A name just for humans
        ,  1024  // This stack size can be checked & adjusted by reading the Stack Highwater
        ,  NULL
        ,  1  // Priority, with 3 (configMAX_PRIORITIES - 1) being the highest, and 0 being the lowest.
        ,  NULL 
        ,  1);
}

void start_TaskVoltage4K()
{
    xTaskCreatePinnedToCore(
        TaskVoltage4K
        ,  "Voltage4K"   // A name just for humans
        ,  4096  // This stack size can be checked & adjusted by reading the Stack Highwater
        ,  NULL
        ,  1  // Priority, with 3 (configMAX_PRIORITIES - 1) being the highest, and 0 being the lowest.
        ,  NULL 
        ,  1);
}




void TaskVoltage15K(void *pvParameters)  
{
    (void) pvParameters;

        /*
        control the voltage of 15KV source with PWM
        */
   

    while (1) 
    {

        


        vTaskDelay(100);  // one tick delay (15ms) in between reads for stability
    }
}


   




/* LEDC (LED Controller) fade example

   This example code is in the Public Domain (or CC0 licensed, at your option.)

   Unless required by applicable law or agreed to in writing, this
   software is distributed on an "AS IS" BASIS, WITHOUT WARRANTIES OR
   CONDITIONS OF ANY KIND, either express or implied.
*/


/*
 * About this example
 *
 * 1. Start with initializing LEDC module:
 *    a. Set the timer of LEDC first, this determines the frequency
 *       and resolution of PWM.
 *    b. Then set the LEDC channel you want to use,
 *       and bind with one of the timers.
 *
 * 2. You need first to install a default fade function,
 *    then you can use fade APIs.
 *
 * 3. You can also set a target duty directly without fading.
 *
 * 4. This example uses GPIO18/19/4/5 as LEDC output,
 *    and it will change the duty repeatedly.
 *
 * 5. GPIO18/19 are from high speed channel group.
 *    GPIO4/5 are from low speed channel group.
 *
 */
#ifdef CONFIG_IDF_TARGET_ESP32
#define LEDC_HS_TIMER          LEDC_TIMER_1
#define LEDC_HS_MODE           LEDC_HIGH_SPEED_MODE
#define LEDC_HS_CH0_GPIO       (18)
#define LEDC_HS_CH0_CHANNEL    LEDC_CHANNEL_0
#define LEDC_HS_CH1_GPIO       (19)
#define LEDC_HS_CH1_CHANNEL    LEDC_CHANNEL_1
#endif
#define LEDC_LS_TIMER          LEDC_TIMER_1
#define LEDC_LS_MODE           LEDC_LOW_SPEED_MODE
#ifdef CONFIG_IDF_TARGET_ESP32S2
#define LEDC_LS_CH0_GPIO       (18)
#define LEDC_LS_CH0_CHANNEL    LEDC_CHANNEL_0
#define LEDC_LS_CH1_GPIO       (19)
#define LEDC_LS_CH1_CHANNEL    LEDC_CHANNEL_1
#endif
#define LEDC_LS_CH2_GPIO       (4)
#define LEDC_LS_CH2_CHANNEL    LEDC_CHANNEL_2
#define LEDC_LS_CH3_GPIO       (5)
#define LEDC_LS_CH3_CHANNEL    LEDC_CHANNEL_3

#define LEDC_TEST_CH_NUM       (2)
#define LEDC_TEST_DUTY         (4000)
#define LEDC_TEST_FADE_TIME    (1000)

void TaskVoltage4K(void *pvParameters)  
{
    (void) pvParameters;


    int ch;

    /*
     * Prepare and set configuration of timers
     * that will be used by LED Controller
     */
    ledc_timer_config_t ledc_timer = {
        .duty_resolution = LEDC_TIMER_13_BIT, // resolution of PWM duty
        .freq_hz = 5000,                      // frequency of PWM signal
        .speed_mode = LEDC_HS_MODE,           // timer mode
        .timer_num = LEDC_HS_TIMER,            // timer index
        .clk_cfg = LEDC_AUTO_CLK,              // Auto select the source clock
    };
    // Set configuration of timer1 for high speed channels
    ledc_timer_config(&ledc_timer);

#ifdef CONFIG_IDF_TARGET_ESP32
    // Prepare and set configuration of timer1 for low speed channels
    
   
#endif
    /*
     * Prepare individual configuration
     * for each channel of LED Controller
     * by selecting:
     * - controller's channel number
     * - output duty cycle, set initially to 0
     * - GPIO number where LED is connected to
     * - speed mode, either high or low
     * - timer servicing selected channel
     *   Note: if different channels use one timer,
     *         then frequency and bit_num of these channels
     *         will be the same
     */
    ledc_channel_config_t ledc_channel = 

        {
            .channel    = LEDC_HS_CH0_CHANNEL,
            .duty       = 0,
            .gpio_num   = LEDC_HS_CH0_GPIO,
            .speed_mode = LEDC_HS_MODE,
            .hpoint     = 0,
            .timer_sel  = LEDC_HS_TIMER 
       
        };

    // Set LED Controller with previously prepared configuration
  
        ledc_channel_config(&ledc_channel);
    

    // Initialize fade service.
    ledc_fade_func_install(0);
    int duty=0;

    while (1) {
        //printf("1. LEDC fade up to duty = %d\n", LEDC_TEST_DUTY);

        duty= get_voltage4K_value()*8191/12;
       // printf("duty= %d", duty);
       
        ledc_set_fade_with_time(ledc_channel.speed_mode,
                    ledc_channel.channel, duty, LEDC_TEST_FADE_TIME);
        ledc_fade_start(ledc_channel.speed_mode,
                    ledc_channel.channel, LEDC_FADE_NO_WAIT);
        
        
       // printf( "free stack =%d\n", uxTaskGetStackHighWaterMark(NULL))  ;

        /*
       ledc_set_fade_with_time(ledc_channel.speed_mode,
                    ledc_channel.channel, duty, LEDC_TEST_FADE_TIME);
        ledc_fade_start(ledc_channel.speed_mode,
                    ledc_channel.channel, LEDC_FADE_NO_WAIT);
        */
        vTaskDelay(LEDC_TEST_FADE_TIME / portTICK_PERIOD_MS);

    
    }
}

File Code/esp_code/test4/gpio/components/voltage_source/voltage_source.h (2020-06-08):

#ifndef VOLTAGE_SOURCE
#define VOLTAGE_SOURCE



void start_TaskVoltage15K();
void start_TaskVoltage4K();



#define PWM_CHANNEL 0
#define PWM_RES 8
#define PWM_PIN 16

#define PWM_FREQ 100

//pwm for gate
#define PULSE_W           50 //lenght of the voltage pulse 50 µS

#define PWM_GATE_CHANNEL  2
#define PWM_GATE_RES      16
#define PWM_GATE_PIN      17

#define PWM_GATE_FREQ       1 //100//1000000/(PULSE_W*10)
#define PWM_GATE_DUTYCYCLE  2//65532  //255/10




#endif

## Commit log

2019-11-30 add pcb from publication
    [1a_Spacers.brd, 1b_Spacer.STL, 200 mm lens half.SLDPRT, 200 mm lens.SLDASM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]
2019-12-01 chore: update boards on pcbway requests
    [1a_Spacers.brd, 2a_Electrodes.brd, 4_Detector.brd, 5_detector backplate.brd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]
2020-03-05 ajout du catia
    [AMPLI.CATPart, DRAWING1.dxf, IMS_COMPLET.CATProduct, IMS_GRID1.CATPart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]
2020-03-05 PCB for voltage divider
    [Divider.kicad_pcb, Divider.sch]
2020-03-05 modif of schematics
    [Ampli_IMS.sch]
2020-03-06 Moved parts
    [Ampli_IMS.kicad_pcb]
2020-03-06 tracks realised
    [Ampli_IMS.kicad_pcb, Ampli_IMS.sch]
2020-03-06 Dimensions of pcb
    Power parts brought together, and length of pcb smaller
    [Ampli_IMS.kicad_pcb]
2020-03-06 Power tracks enlarged
    [Ampli_IMS.kicad_pcb]
2020-03-06 Signal tracks enlarged
    [Ampli_IMS.kicad_pcb]
2020-03-06 Begin PCB of divider
    [Divider.sch, DividerV2.sch]
2020-03-07 Pbs with footprints
    [DividerV2.kicad_pcb, DividerV2.sch]
2020-03-07 PCB + new electrodes
    [DividerV2.kicad_pcb, DividerV2.sch]
2020-03-07 1st pcb done
    [DividerV2.kicad_pcb, DividerV2.sch]
2020-03-07 added tips about low noise pcb design
2020-03-08 catia update
    [AMPLI.CATPart, IMS_COMPLET.CATProduct, IMS_GRID1.CATPart, IMS_GRID1_2.CATPart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]
2020-03-08 Divider1: Without tracks
    [Divider1.sch]
2020-03-08 Dividers finished without testing points
    [Divider1.kicad_pcb, Divider2.kicad_pcb]
2020-03-08 Divider finished with test points
    [Divider1.kicad_pcb, Divider2.kicad_pcb]
2020-03-08 Most parts completed
    [Alim_and_ctr.sch, Divider1.sch, Divider2.kicad_pcb, Divider2.sch]
2020-03-09 low noise pcb design
    [Ampli_IMS.kicad_pcb]
2020-03-10 Small corrections
    [Alim_and_ctr.sch, Divider1.sch]
2020-03-10 Revert "Small corrections"
    [Alim_and_ctr.sch, Divider1.sch]
2020-03-10 Low noise smd amp
    [Ampli_IMS.kicad_pcb, Ampli_IMS.sch]
2020-03-10 SMD + low noise design
    [Ampli_IMS.kicad_pcb, Ampli_IMS.sch]
2020-03-11 low noise features
    [Ampli_IMS.kicad_pcb]
2020-03-11 Small mistakes
    [Ampli_IMS.kicad_pcb, Ampli_IMS.sch]
2020-03-11 pcd target added
    [cible.kicad_pcb, cible.sch]
2020-03-21 GND guards are neat!
    [Ampli_IMS.kicad_pcb, Ampli_IMS.sch]
2020-03-22 Implementation of the HV sources footprints and schems
    [Alim_and_ctr.sch, Divider1.sch, Divider2.sch]
2020-03-24 Small modifications
    [Alim_and_ctr.sch, Complete_divider.sch, Divider1.sch, Divider2.sch]
2020-03-25 Implementing MCU
    [Alim_and_ctr.sch]
2020-03-25 Labelling/ordering stuff
    [Alim_and_ctr.sch]
2020-04-08 DC/DC isolated converter implementation
    [Alim_and_ctr.sch, Complete_divider.sch]
2020-04-09 Set a Vin of 5V
    [Alim_and_ctr.sch, Complete_divider.sch]
2020-04-09 Small changes
    [Alim_and_ctr.sch]
2020-04-09 Implementation of ESP32 code
2020-04-17 New isolated alimentation design
    [Alim_and_ctr.sch]
2020-04-29 Modifications of the amplification part
    [Alim_and_ctr.sch]
2020-06-01 Voltage measure circuits
    [Alim_and_ctr.sch, Complete_divider.sch, Divider1.sch, Divider2.sch]
2020-06-02 Begin PCB design
    [Alim_and_ctr.kicad_pcb, Alim_and_ctr.sch, Complete_divider.sch, Divider1.sch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]
2020-06-02 Components in place
    [Alim_and_ctr.kicad_pcb, Alim_and_ctr.sch]
2020-06-05 Electrode design
2020-06-05 HV design finished
    [Alim_and_ctr.kicad_pcb, Alim_and_ctr.sch, Complete_divider.sch]
2020-06-08 Improve PCBs
    [Alim_and_ctr.kicad_pcb, Alim_and_ctr.sch, Ampli_IMS.kicad_pcb, Ampli_IMS.sch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]
2020-06-08 code update: final file is in test4
    [partitions_example.csv]
2020-06-11 Ampli last version - low noise guarding
    [Ampli_IMS.kicad_pcb]
2020-06-11 Alim&control update
    [Alim_and_ctr.kicad_pcb, Alim_and_ctr.sch, VoltageMeas&ManualCtrl.sch, VoltageMeasurements.sch]
2020-06-12 Updates of dividers 1 & 2
    [Divider1.kicad_pcb, Divider1.sch, Divider2.kicad_pcb, Divider2.sch]
2020-07-13 Complete divider update
    [Alim_and_ctr.kicad_pcb]
2023-06-01 Add new CAD files version V2
    New CAD files for version V2 of 3D printed IMS. New folders created to reorganize CAD files in efficient way.
    [AMPLI.CATPart, Cible.3MF, Cible.SLDPRT, Cible.STEP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]
2023-06-08 Add V3 IMS CAD version
    [Assembly_grid_shutter.SLDASM, Cible.SLDPRT, Cible_region_gas.3MF, Cible_region_gas.SLDPRT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]

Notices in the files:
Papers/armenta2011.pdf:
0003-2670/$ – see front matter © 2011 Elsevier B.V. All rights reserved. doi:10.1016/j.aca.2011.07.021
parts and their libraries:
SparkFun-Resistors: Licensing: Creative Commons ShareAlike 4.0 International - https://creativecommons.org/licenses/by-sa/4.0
